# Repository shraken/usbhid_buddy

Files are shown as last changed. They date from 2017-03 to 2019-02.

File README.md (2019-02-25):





# Buddy DAQ

Buddy is a free, open source, and low-cost data acquisition (DAQ) instrument.  It has 8 configurable
IO that can be configured for ADC, DAC, PWM, or counter operation.  The device uses USB HID with a 
custom descriptor for communication with the hidapi library on the host system.  The device can be 
configured as either a host polled or asynchronous update mode for maximum flexibility.  Buddy works
on linux, windows, and macOS systems.  

## Docker

Usage of docker is recommended for building the entire project.  A CMakeList file is provided in the head
directory to build the project and generate all support files (documentation, coverage reports). 

```shell
docker build -t buddy_docker .
docker run -v /path/to/usbhid_buddy:/docker -it buddy_docker /bin/bash
```

this will launch a Docker bash shell and then you build.

```shell
cd /docker
mkdir -p build
cd build
cmake ..
make
```

## Firmware

The firmware is written in C for the Silicon Labs C8051F380/EFM8UB2 chip and is in the `fw` directory.  The
firmware requires a Keil C51 compiler to be used for building.  

The open-source [gboot](https://github.com/shraken/gboot) bootloader written by Gabriele Gorla of gglabs (http://gglabs.us) is used for the buddy device. 

## Hardware

The hardware is developed using the KiCad EDA tool.  The manafacturing, source, and schematic
files are provided in the hw/ directory.

The pin mapping for the standard Bus Pirate 10-pin harness is provided below:

| Color         | Mapping   | Pin #  |
| ------------- |:---------:|:------:|
| Brown         | IN7       |     2  |
| Red           | GND       |     1  |
| Orange        | IN6       |     4  |
| Yellow        | IN5       |     3  |
| Green         | IN0       |     6  |
| Blue          | IN4       |     5  |
| Purple        | IN2       |     8  |
| Grey          | IN1       |     7  |
| White         | 3.3V      |    10  |
| Black         | IN3       |     9  |

## Software

The host software uses the free and open source hidapi library for driverless
operation.  The examples provided build with the hidapi libray itself and
are tested on Linux, Windows, and mac OS systems.

For building the host examples, the hidapi submodule must be cloned with the
following command:

`git submodule update --init`

or when cloning the buddy repo with:

`git clone --recursive https://github.com/shraken/usbhid_buddy.git`

## Tests

The `tests` directory contains the unit tests.  The [Catch2](https://github.com/catchorg/Catch2) test
framework is used for all unit tests.  To manually build and run the unit test, run the following:

```shell
cd tests/
mkdir -p build
cd build
cmake ..
make
./testLibBuddy
```

## Code Coverage

The build server runs gcov/lcov to generate the coverage figure.  You can collect these results manually
by running the following (from the build directory in `tests`):

```shell
lcov -c -d CMakeFiles -out cov.info
genhtml cov.info -o out
open out/index.html
```

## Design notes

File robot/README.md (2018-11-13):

# Buddy Test Platform

This repo contains the manufacturing automated test system for the Buddy USB HID DAQ hardware
device.  

The automated test board mates with a Teensy 3.6 microcontroller for measurement and
stimulus of the "Buddy" DAQ under test.
 - `teensy/` - teensy Arduino firmware for the DUT test software
 - `sw/` - host based robot framework source files to be run by tester
 - `hw/` - PCB schematic, layout, and datasheet files

# Requirements

Install the [ADC](https://github.com/pedvide/ADC) library for the Arduino software.  

# Building

There is no automated build procedure.  

1. Open Arduino IDE 

Modify the `RingBuffer.h` file and set the define `RING_BUFFER_DEFAULT_BUFFER_SIZE` to 4096.  This
requires modification of the `RingBuffer.h` file provided in the `ADC` library installed above.  

# Usage

on Windows

```shell
cd sw/
./run_tests.bat
```

on Linux and Mac OS

```shell
cd sw/
./run_tests.sh
```

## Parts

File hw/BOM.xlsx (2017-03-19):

Id | Designator | Package | Quantity | Designation | Supplier and ref | Cost (quantity 1) | Total Cost | Comments
1 | R5,R2,R8,R9,R3,R14 | R_0603_HandSoldering | 6 | 1k | 667-ERJ-3EKF1001V | 0.15 | 0.9
2 | C1,C3,C6,C7,C10,C11,C12,C13,C16 | C_0603_HandSoldering | 9 | 100nF | 81-GRM39X104K25 | 0.1 | 0.9
3 | C2,C4,C5,C9 | C_0805_HandSoldering | 4 | 1uF | 810-C2012X7R1E105K | 0.14 | 0.56
4 | C8,C14 | C_0603_HandSoldering | 2 | 1uF | 81-GRM188R61E105KA12 | 0.1 | 0.2
5 | C15 | C_0603_HandSoldering | 1 | 10uF | 81-GRM188R60J106KE7D | 0.13 | 0.13
6 | C10 | C_0603_HandSoldering | 1 | 4.7uF | 81-GRM18R60J475KE19D | 0.11 | 0.11
7 | R1 | R_0603_HandSoldering | 1 | 100R | 660-RK73H1JTTD1000F | 0.1 | 0.1
8 | R2,R3,R5,R8,R9,R14 | R_0603_HandSoldering | 6 | 1k | 667-ERJ-3GEYJ102V | 0.1 | 0.6
9 | R6,R7,R10,R15,R16,R17 | R_0603_HandSoldering | 6 | 10k | 667-ERJ-3GEYJ103V | 0.1 | 0.6
10 | R11 | R_0603_HandSoldering | 1 | 0R_NM | 667-ERJ-3GEY0R00V |  | 0 | NM
11 | R4,R12,R13 | R_0603_HandSoldering | 3 | 0R | 667-ERJ-3GEY0R00V | 0.1 | 0.3
12 | D1,D2 | LED_0603 | 2 | LED | 720-LGQ396A3964 | 0.19 | 0.38
13 | D3 | PRTR5V0U2X,215 | 1 | PRTR5V0U2X,215 | 771-PRTR5V0U2X-T/R | 0.52 | 0.52
14 | D4,D5,D6,D7,D8,D9,D10,D11 | SOT-23 | 8 | D_Schottky_x2_Serial_AKC | 512-BAT54S | 0.24 | 1.92
15 | DN1 | LTST-C195KGJRKT | 1 | LTST-C195KGJRKT | 859-LTST-C195KGJRKT | 0.4 | 0.4
16 | F1 | R_1206 | 1 | 1206L050/15YR | 576-1206L075/13.2WR | 0.49 | 0.49
17 | U1 | SOT-23-5 | 1 | MCP1802T-3302I/OT | 579-MCP1802T-3302IOT | 0.58 | 0.58
18 | U2 | LQFP-48_7x7mm_Pitch0.5mm | 1 | C8051F380 | 634-8UB20F64GAQFP48 | 1.9 | 1.9
19 | U3 | TSSOP-20_4.4x6.5mm_Pitch0.65mm | 1 | TLV5630 | 595-TLV5630IPW | 20.12 | 20.12
20 | U4 | VSSOP8-DGK | 1 | TPS60241 | 595-TPS60241DGKR | 1.63 | 1.63
21 | U5 | SOT-23 | 1 | REF3325AIDBZR | 595-REF3325AIDBZR | 1.8 | 1.8
22 | U6 | TSSOP-8_4.4x3mm_Pitch0.65mm | 1 | 23LC1024-I/ST | 579-23LC1024-I/ST | 2.57 | 2.57
23 | U7,U8 | SOT-23-5 | 2 | 74AHC1G125 | 595-SN74AHC1G125DBVR | 0.41 | 0.82
24 | USB1 | microb_usb_top_mount | 1 | MICRO-B_USB | 538-47346-1001 | 0.73 | 0.73
25 | SW1,SW2 | SKRKAEE010 | 2 | SKRKAEE010 | 688-SKRKAE | 0.48 | 0.96
26 | P1 | Socket_Strip_Straight_1x02 | 1 | CONN_01X02 |  |  | 0
27 | P2 | Socket_Strip_Straight_1x03 | 1 | CONN_01X03 |  |  | 0 | NM
28 | P3 | Molex_PicoBlade_53261-0371 | 1 | CONN_01X03 | 538-53261-0371 | 0.9 | 0 | NM
29 | P4 | Socket_Strip_Angled_2x05 | 1 | CONN_02X05 | 571-5103308-1 | 0.74 | 0.74 | NM
 |  |  |  |  |  | parts total | 39.96
 | Manafacturing |  |  |  |  | placements | 68
 | Board Size: |  |  | per |  | unique parts | 29
 | 64x37mm | smartprototyping | $146/100 | 1.46
 |  |  | $1000/1000 | 1
 | Assembly | smallbatchassembly | quantity 100 | 10.74
 |  |  | quantity 1000 | 5.25
 | Others
 |  | Acrylic Case | 110990059 | 3 | https://www.seeedstudio.com/Bus-Pirate-v4-Acrylic-case-kit-v1-p-1417.html
 |  | IDC ribbon cable | CAB-09556 | 4.95 | https://www.sparkfun.com/products/9556
 | total cost | 52.16

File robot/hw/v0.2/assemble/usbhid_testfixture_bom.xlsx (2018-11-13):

Title | usbhid_testfixture |  |  | Digikey
Revision | v0.1
Date | 2017-12-10
Generated | 2017-12-10
Company | Wiggle Labs
Comment 1
Comment 2
Comment 3
Comment 4
Total Parts | 18
Total Unique Parts | 9
Ref | Qty | Value | Footprint
C1 C2 C3 | 3 | 0.1uF | Capacitors_SMD:C_0603_HandSoldering | 399-1096-1-ND
J1 J2 | 2 | Conn_01x14 | Socket_Strips:Socket_Strip_Straight_1x14_Pitch2.54mm | S9195-ND
J3 | 1 | Conn_01x05 | Socket_Strips:Socket_Strip_Straight_1x05_Pitch2.54mm | S6103-ND
J4 | 1 | Conn_02x05_Odd_Even | Socket_Strips:Socket_Strip_Straight_2x05_Pitch2.54mm | A33159-ND
P1 | 1 | BTE-020-01-F-D | samtec:BTE-020-01-F-D-A | SAM10934-ND
R1 R2 R3 R4 R5 | 5 | 10k | Resistors_SMD:R_0603_HandSoldering | 311-10KGRCT-ND
U1 U2 | 2 | MAX335 | Housings_SSOP:TSSOP-24_4.4x7.8mm_Pitch0.65mm | MAX335EUG+-ND
U5 | 1 | MAX4617 | Housings_SSOP:TSSOP-16_4.4x5mm_Pitch0.65mm | MAX4617CUE+CT-ND
U4 U3 | 2 | 74AHC1G125 | TO_SOT_Packages_SMD:SOT-23-5 | 74AHC1G125W5-7DICT-ND
BOM made with KICAD_BOM_WIZARD (https://github.com/HashDefineElectronics/KiCad_BOM_Wizard.git)
Generated 12/10/2017 6:05:52 PM

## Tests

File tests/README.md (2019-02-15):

# Testing

## Unit Tests

We use the Catch-2 test framework to write the unit tests.  The unit tests test the internal logic
and mock out physical hardware access with dummy stubs that we can check were called.  

The units test are written for the following components:
 - codec
 - buddy host library

 Future:
  - firmware
  - python bindings
  - any future language binding

The unit tests are configured to run with the CI and a coverage report is generated and reported on
coveralls hosted site.  Future plan for manual HTML generation are being made.

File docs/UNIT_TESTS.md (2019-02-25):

lib/libbuddy/
 - utility(.h/.c):
  * debug_init
  * debug_write
  * debug_cleanup

 - usbhid_buddy(.h/.c):
  x * reset_codec
  x * encode
  x * decode
  * hidapi_init
  * buddy_write_raw
  * buddy_write_packet
  * buddy_read_packet
  * buddy_send_generic
  * buddy_read_generic
  * buddy_read_generic_noblock
  * buddy_send_pwm
  * buddy_send_dac
  * buddy_read_counter
  * buddy_read_adc
  * buddy_read_adc_noblock
  * buddy_clear
  * buddy_flush
  * buddy_count_channels
  * buddy_configure
  * buddy_get_response
  * buddy_reset_device
  * buddy_get_firmware_info
  * buddy_init
  * buddy_trigger
  * buddy_cleanup

 - support(.h/.c):
  x * swap_uint16
  x * swap_int16
  x * swap_uint32
  x * swap_int32
  x * short_sleep

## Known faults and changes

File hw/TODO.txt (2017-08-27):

v0.5:

 * make micro USB footprint with slotted holes and replace Molex part
 * fix footprint for ESD USB protection diode
 * fix footprint for bicolor red/green LED DN1
 * fix fotprint for TPS 5V converter
 * add fidiucials
 * revert back to SOT23-5 footprint for tristate buffer SN74AHC1G125
 * establish if polyfuse is appropriate given max current of LDO 3.3V reg
 * add testpad for GPIO that can be used for timing
 * consider adding mezzanine on bottom side of board for future
   expander boards

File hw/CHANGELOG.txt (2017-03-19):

v0.1:
* frist!!! release
----

v0.2:
x1. shrink size back down a bit
x2. see if can get away with a 2 layer with GND and +3.3V pour on TOP/BTTM
x3. footprint fixes
   a. 10 pin header needs a silkscreen outline for pins. center and move over.
x4. fix C8051F380 bad pin 12 with 100R to GND when it really should go
   to VBUS.
x5. footprint for the ESD protection diode is bad needs to be fixed
x6. footprint for +5V regulator/reference should be widened for pads
x7. the location of the 10-pin 2 row header is wacky and should be centered
x8. look into mechanical enclosure for entire unit with eye to remove 
  dual row headers.

  alternatively adopt the bus pirate mech footprint standard.

**RESIZED to BUS PIRATE V3.6 FOOTPRINT**

XX9. (potentially use ADG1414BRUZ-REEL7 as an octal SPST switch to isolate DAC
       and ADC so they can coexist on same pins) or MAX335 or MAX395.

** ATTEMPT IN SOFTWARE TO VERIFY IF DAC CAN BE POWERED OFF AND SAME ATTACHED
  CHANNEL USED AS ADC WITH EXTERNAL VOLTAGE STIMULUS **

not required, will not be implemented in v0.2

x10. USB VBUS power LED indicator
x11. change the micro USB connector out for the EOL Hirose to a a standard SMD
   mount with a non-reversed connector

Amphenol-FCI 10118192-0001LF
609-4613-1-ND
http://www.digikey.com/product-detail/en/10118192-0001LF/609-4613-1-ND/2785378?WT.z_cid=ref_octopart_dkc_buynow&site=us

https://github.com/open-project/kicadlibrary
----

v0.3:
1. rearrange buttons and LEDs to fit the existing enclosure footprint
x2. move 10 pin header back 1.1 mm to fit into enclosure.  size check
x3. fix the USBDP and USBDN routing issue
x4. make footprint for TPS 5V reference larger
-?5. make footprint for dual color LED slightly larger
x6. rounded edge corners
x7. make corner holes larger, 2.7mm -> 3.2mm+ **(made to 3.2mm PAD)
x8. make red/green bicolor LED active low
x9. move ADC0_IN and ADC1_IN to P0.6 and P0.7 for interrupt capability
x10. look into benefit of additional crystal oscillator for timing tolerance improvement
 (added a 32.768 kHz watch crystal for millis timer and ADC sampling trigger clock)
----

v0.4:
x1. add SPI SRAM buffer
?2. fix bad GND pour DRC issued with pin 6 on chip U2.
-3. make USB1 connector to use slotted holes for mechanical robustness (not this revision)
x4. add protection diodes to ADC and DAC channels
x5. add picoblade programming header on bottom of board to mate to C2 adapter board
x6. switch ADC0_IN and ADC1_IN from P0.6 and P0.7 as they can't be allocated for ADC
x7. add a USB polyfuse
x8. add SPI testpads on backside of board
x9. add health indicator LED for 1 second interval flashing
-10. add testpoint for spare GPIO
NO 11. switch red and green bicolor LED back to active high cfg
x12. remove watch crystal
x13. make VREF (P1.5) connected to a 2.5V reference
x14. add MISO connection to read out TLV563x parameters
x15. add tristate buffer to MISO/SOMI lines for TLV563x and 23LC1024 module 
x16. fix incorrect naming scheme, DAC_OUTA = ADC0_IN
NO 17. consider backside mezzanine connector to mate for mating to a breakout DB
	or bulk screw-terminal board.
x18. add 10 uF and 100 pF decoupling cap on PIN16 of TLV563X for internal voltage ref
  as recommended by the datasheet. 
x19. add 4.8 uF and 0.1 uF bypass capacitor on P1.5 reference pin on C8051F380 chip
----

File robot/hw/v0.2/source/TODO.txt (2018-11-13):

v0.2:
 x * resisitive divider from FIO pins on the ADC.  Place the divider network
   on the ADC pin side of the multiplexor.  The divider should bring 5V max
   to 3.3V.
 x * LED indicators on board driven by Teensy to indicate when test is ongoing
 and maybe a visual indicator for pass/fail.
 x * replace teensy 3.2 with teensy 3.6 for the the additional RAM and CPU.
 (NO) consider usage of secondary ADC and DAC as a means to perhaps scan for
  crosstalk measurements.
 x * use +5V logic almost everywhere.  Replace 3.3V with 5.0V on MAX335 and
 MAX4617..
 (THERE) consider SD card access to save logs on teensy?
* test points or some secondary header to expose FIO_0 - FIO_7 for
saleae analyzer.

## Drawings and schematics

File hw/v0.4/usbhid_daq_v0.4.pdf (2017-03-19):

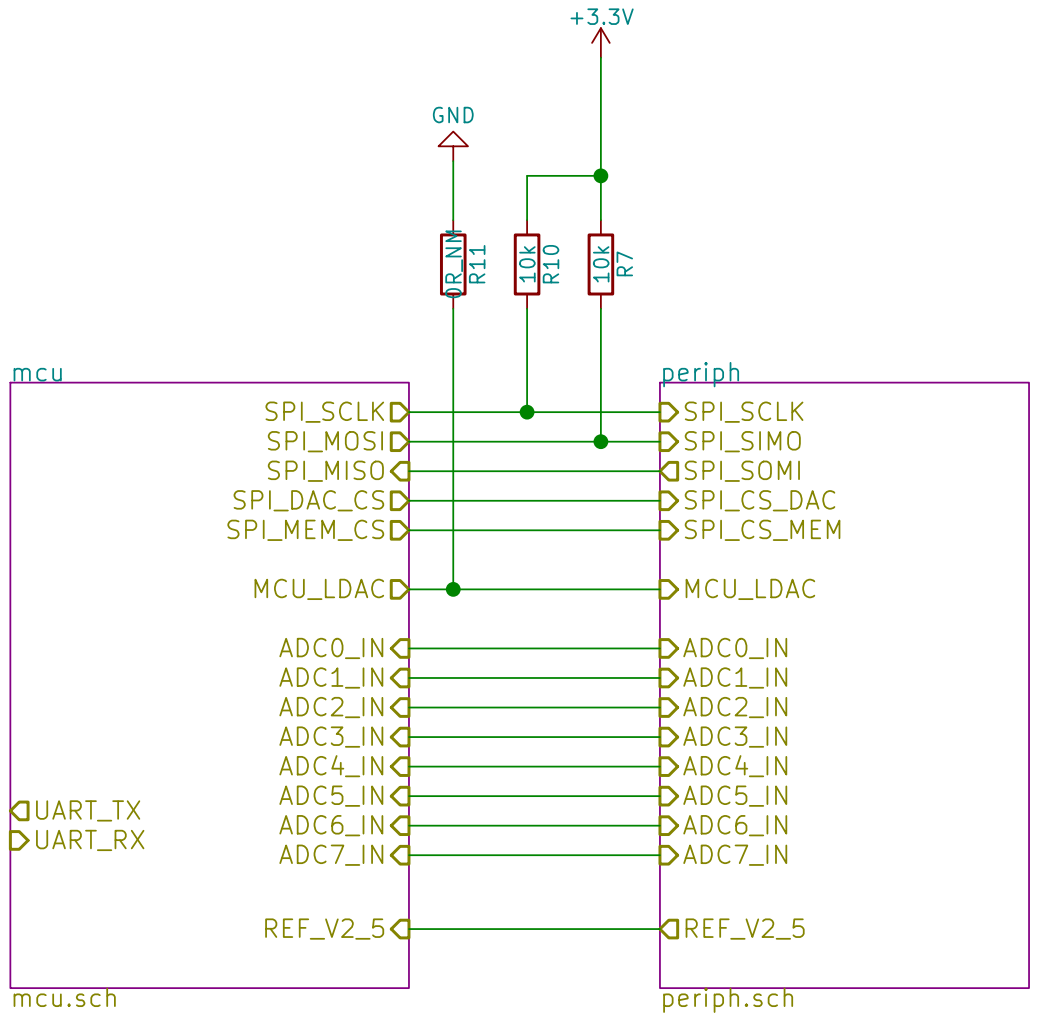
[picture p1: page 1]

File: usbhid_daq.sch Sheet: / Wiggle Labs

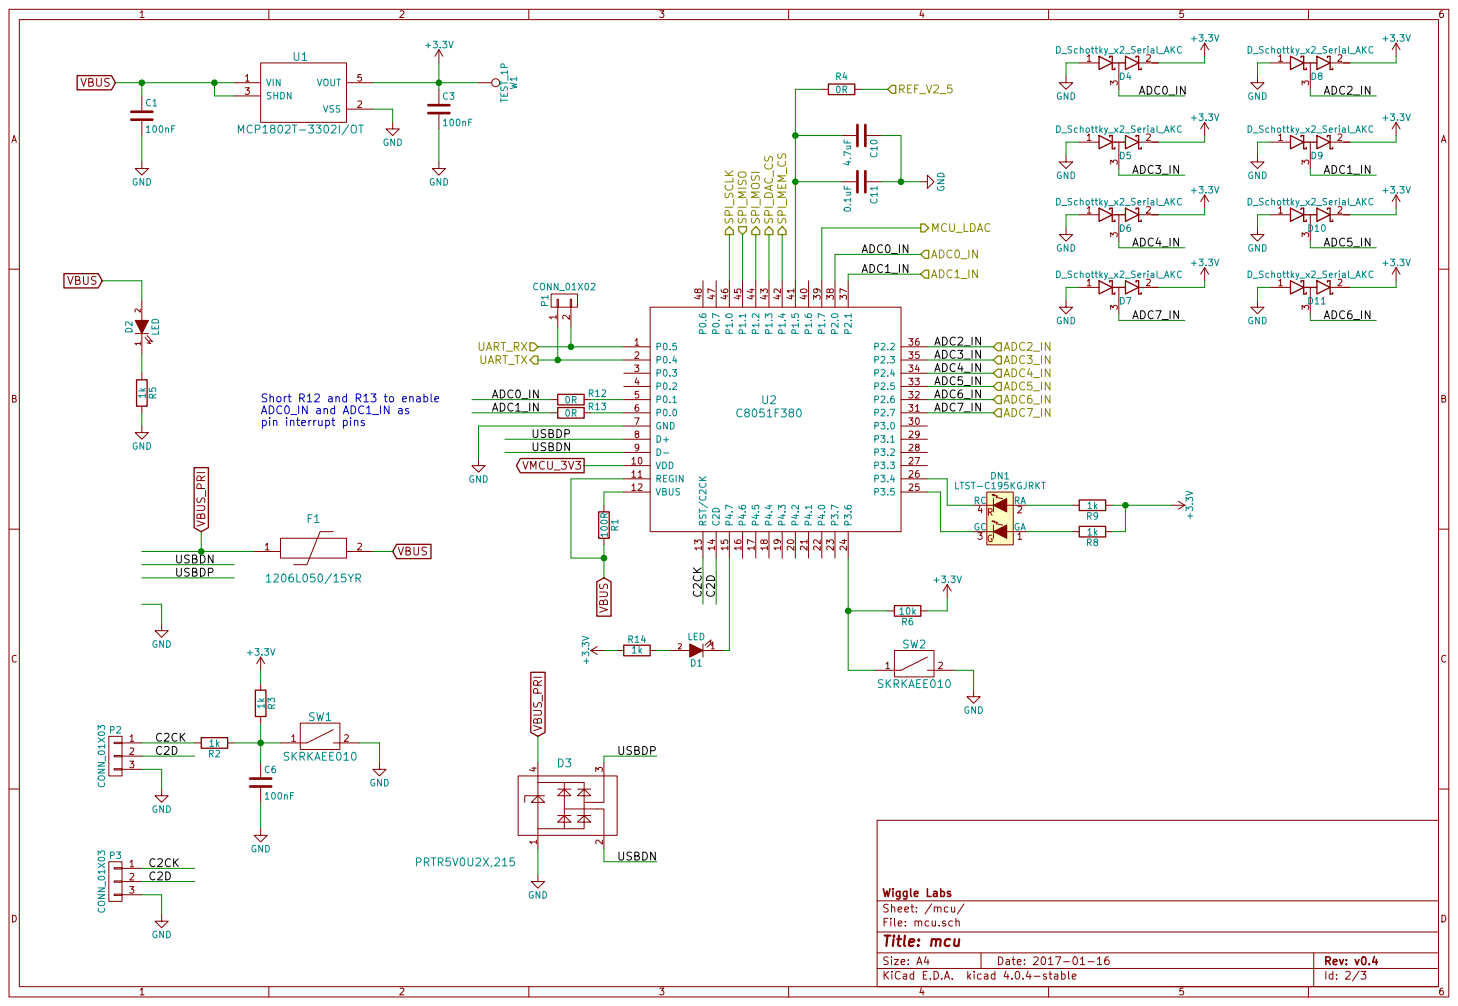
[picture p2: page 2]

1 2 D2 LED 1kR5 GND VBUS VBUS

Short R12 and R13 to enable
ADC0_IN and ADC1_IN as

File: mcu.sch Sheet: /mcu/ Wiggle Labs

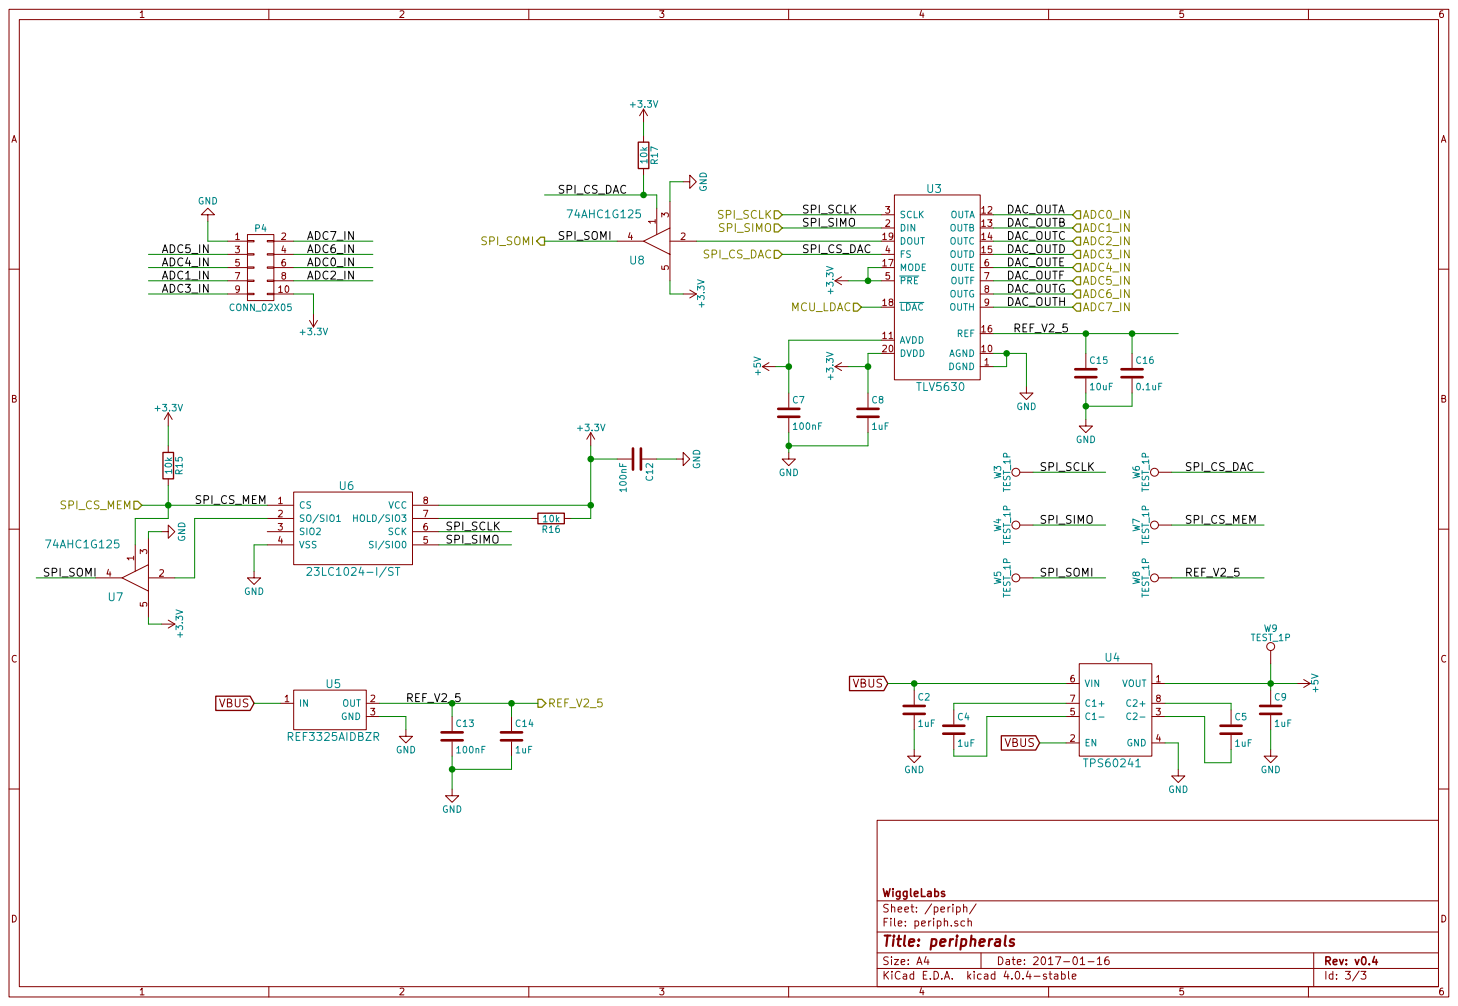
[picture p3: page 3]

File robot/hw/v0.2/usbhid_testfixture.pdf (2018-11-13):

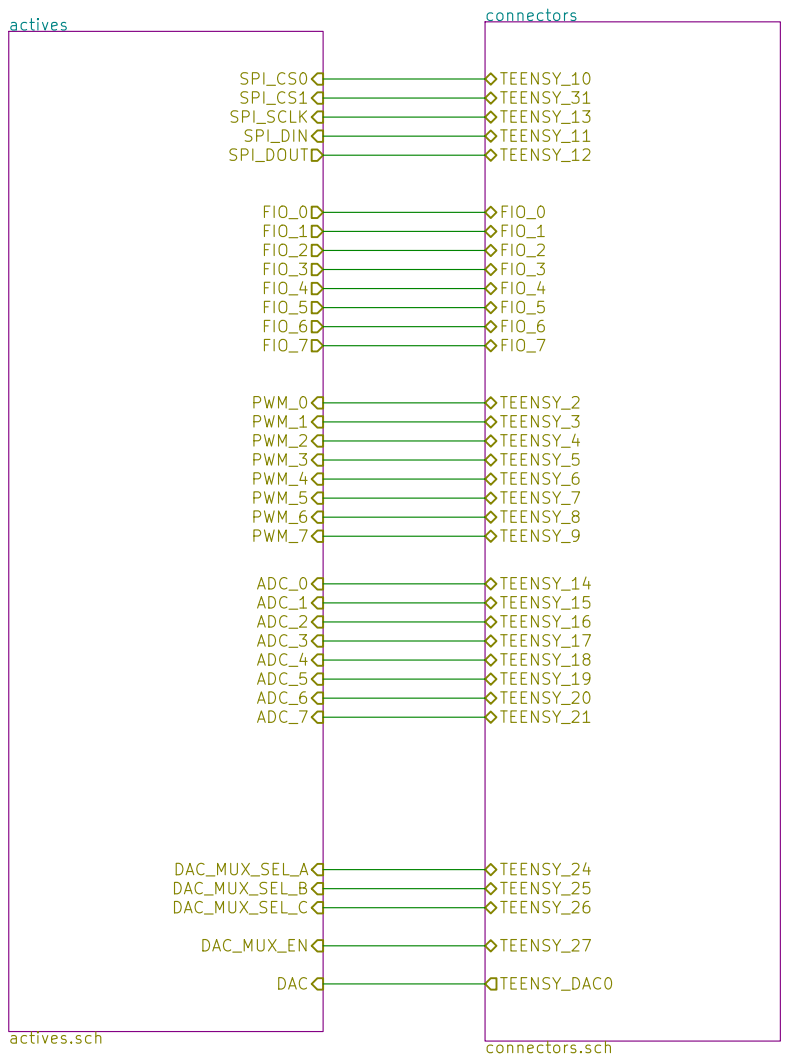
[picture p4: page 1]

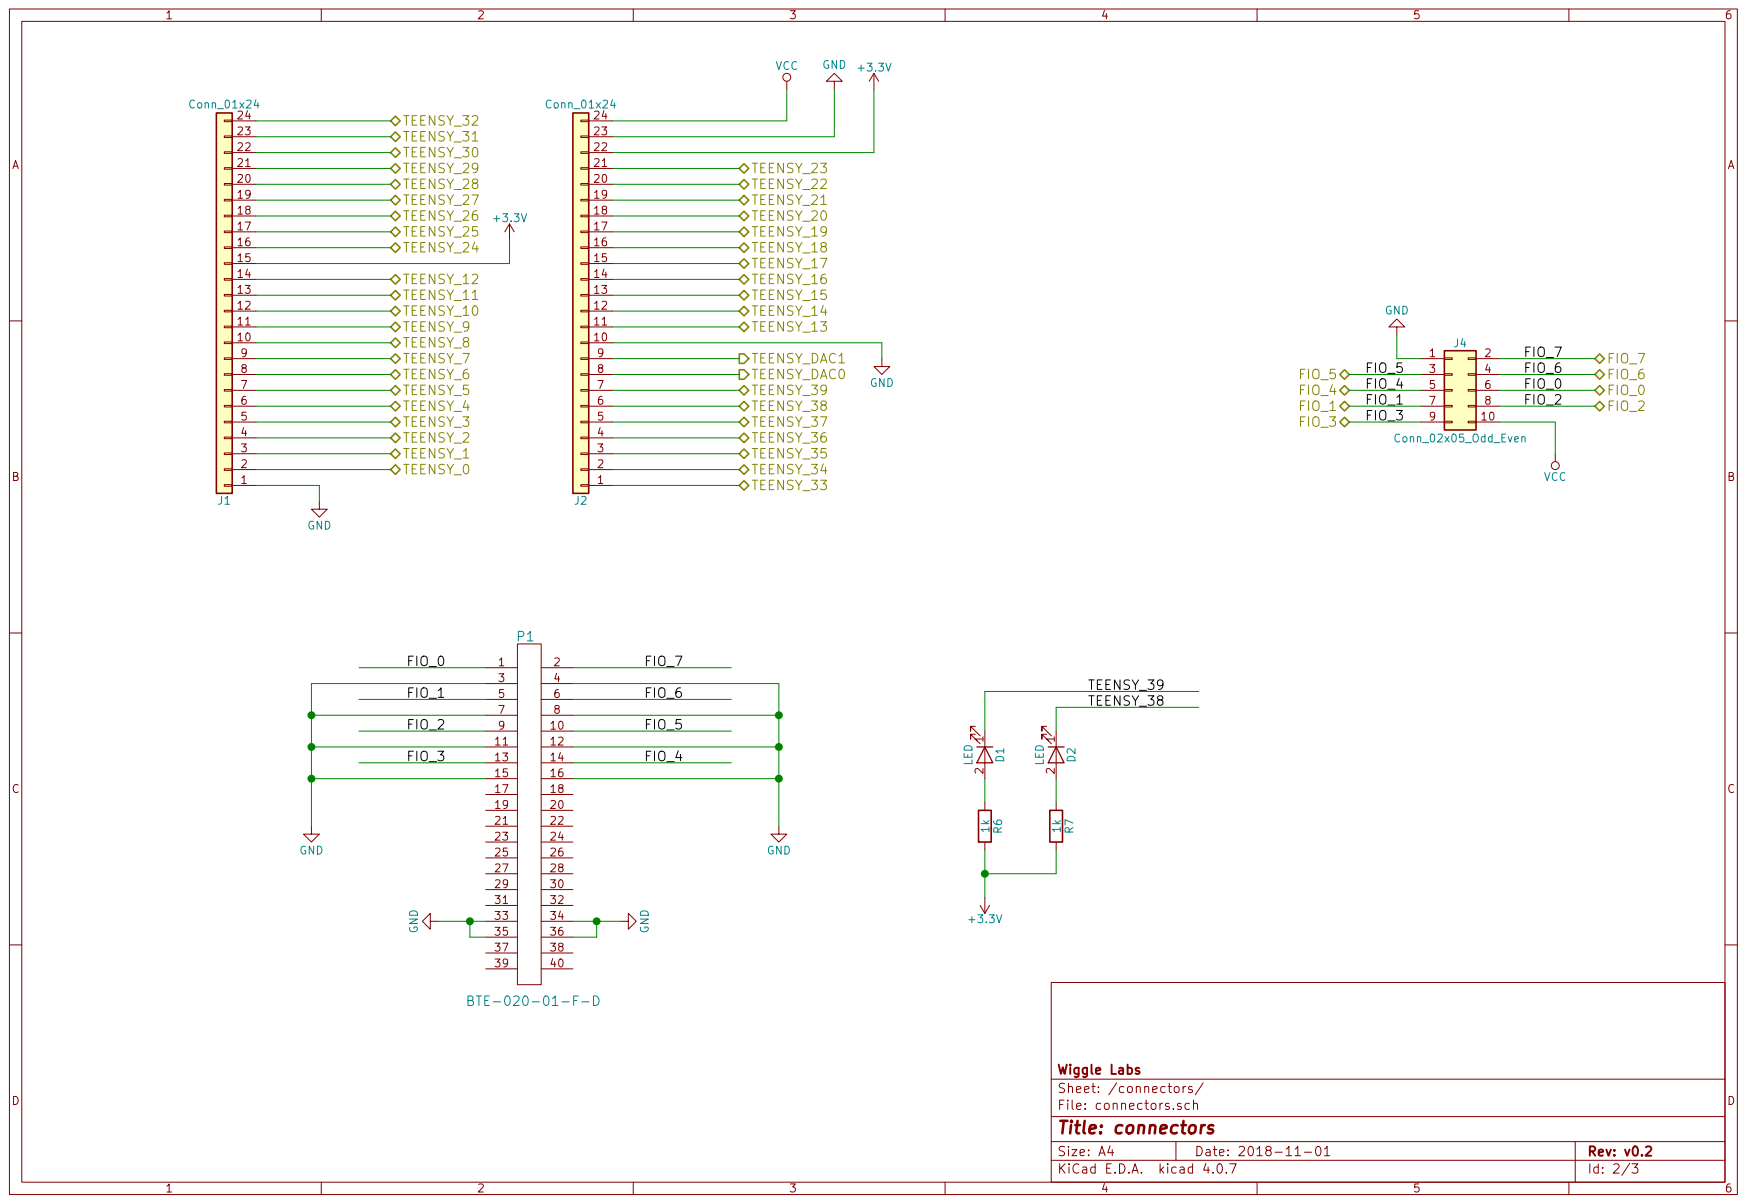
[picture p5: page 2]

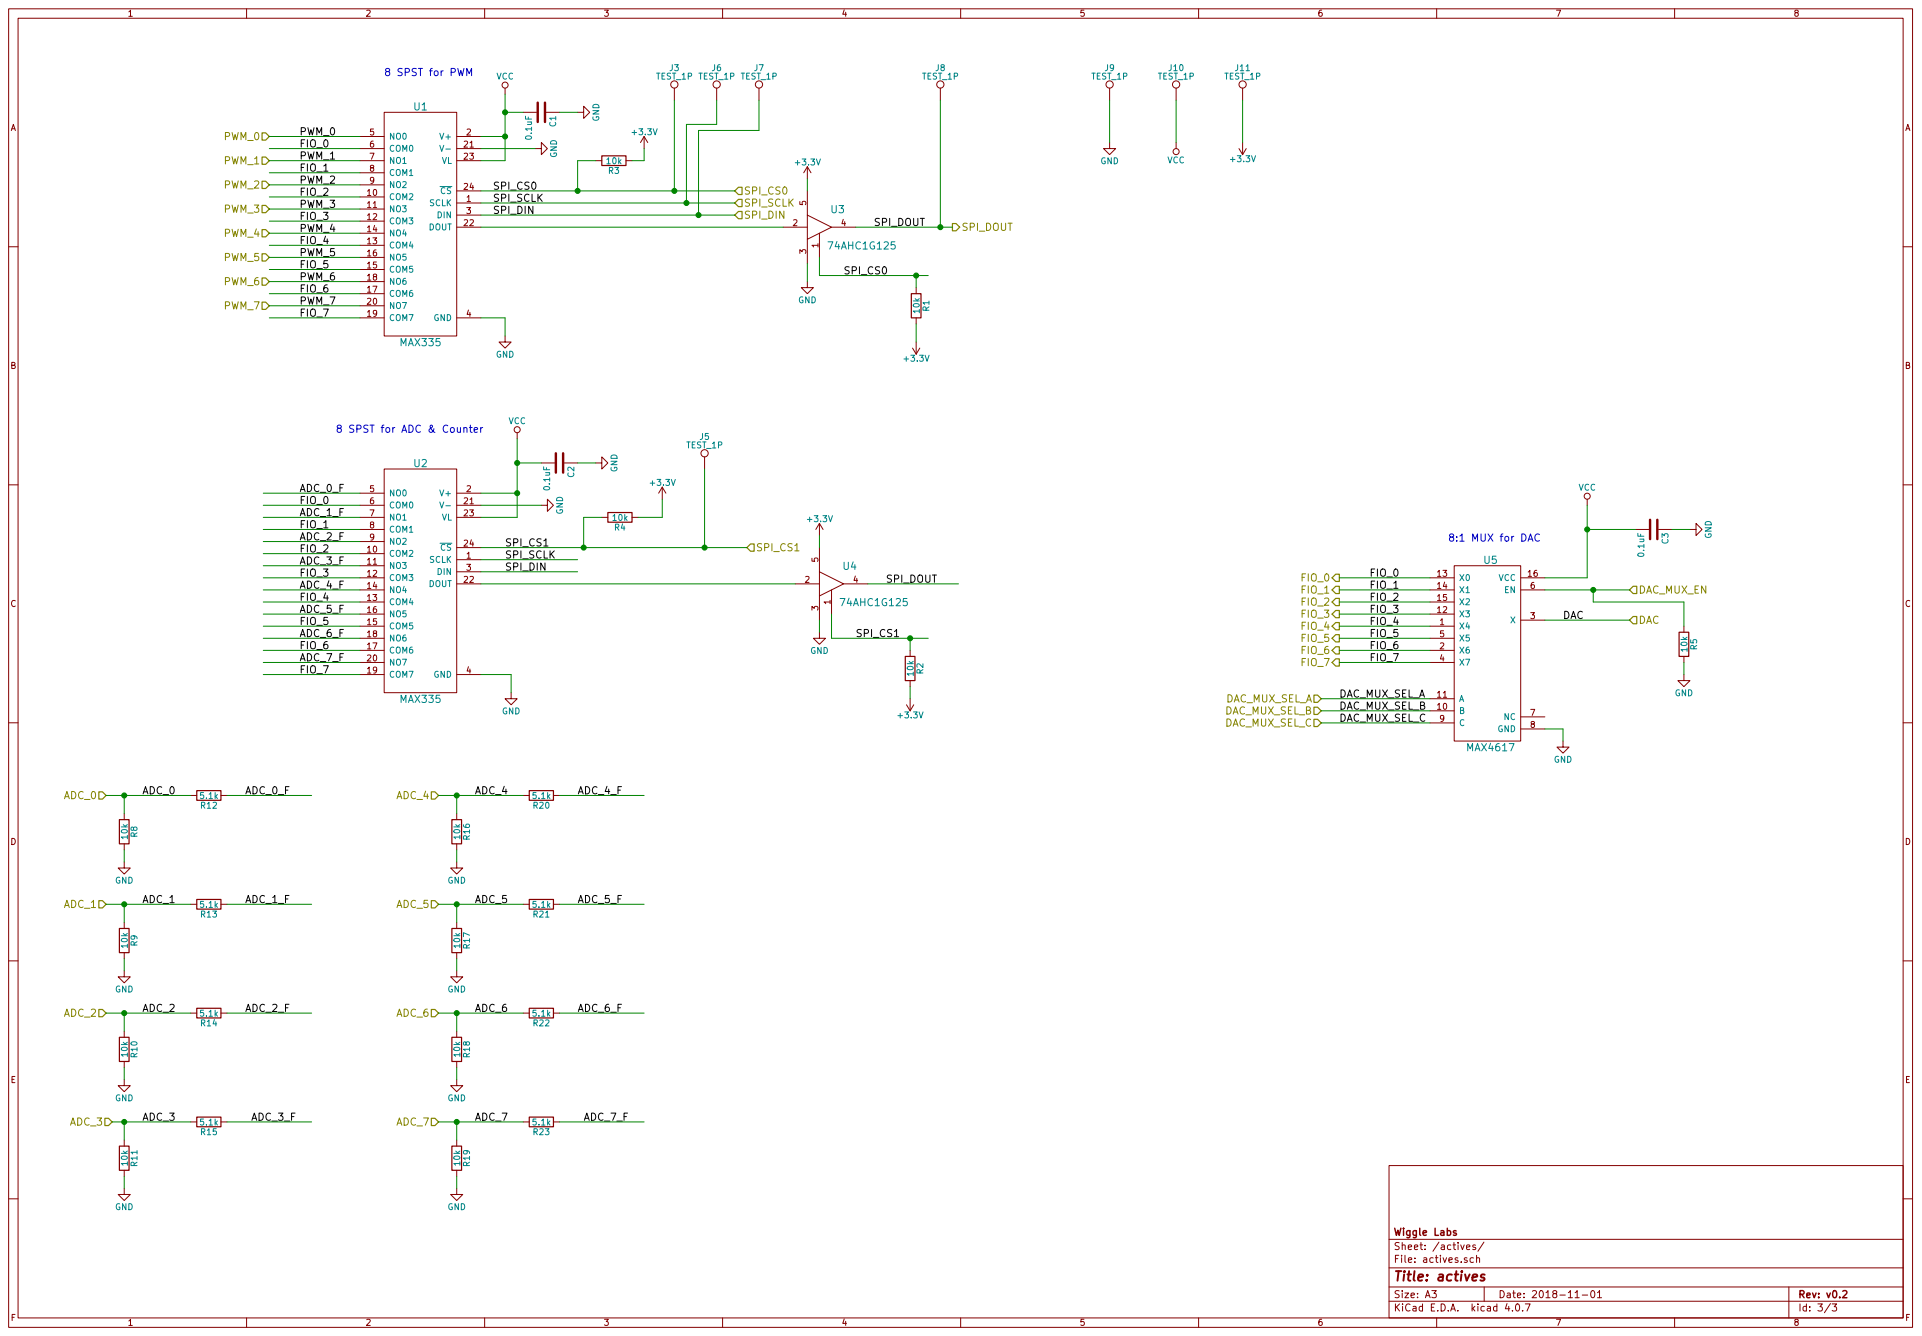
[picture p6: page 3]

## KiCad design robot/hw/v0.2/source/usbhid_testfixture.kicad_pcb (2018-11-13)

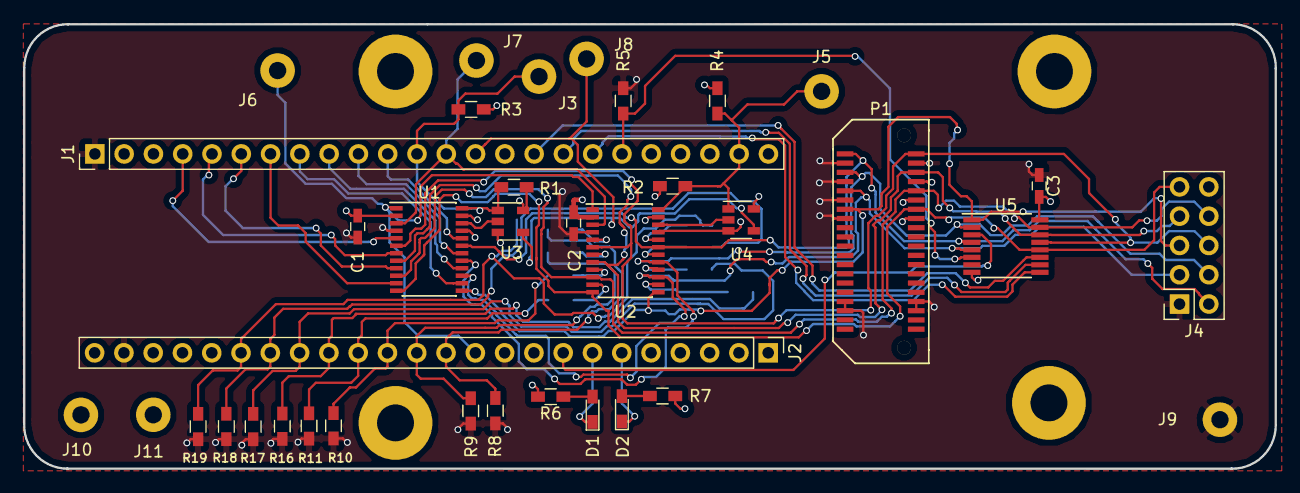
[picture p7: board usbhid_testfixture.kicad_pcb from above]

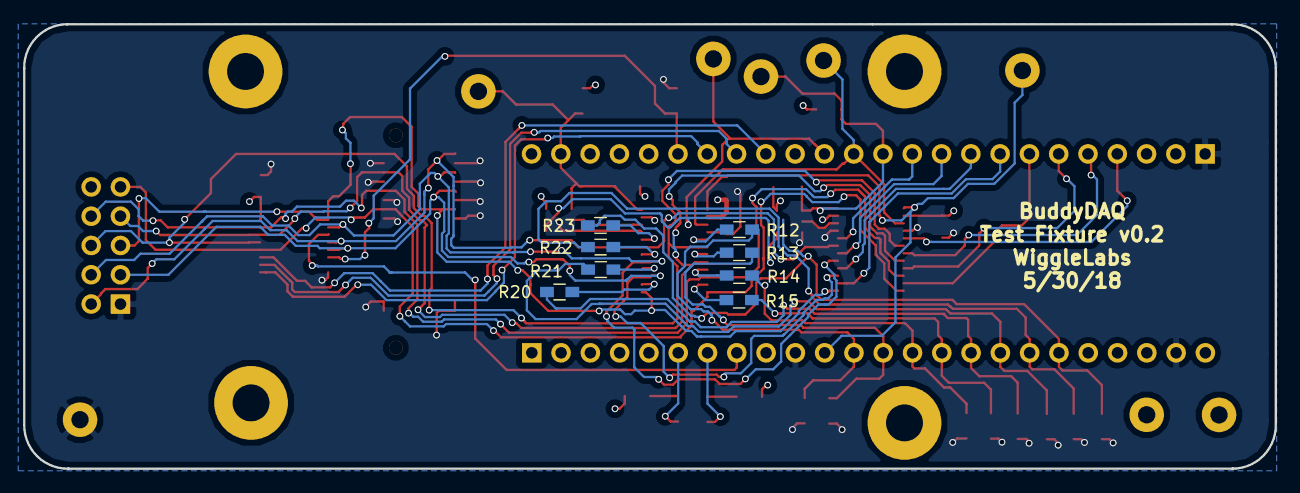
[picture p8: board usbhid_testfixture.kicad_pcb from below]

Board: 4 copper layers, 108.5 x 38.5 mm, 45 parts (8 on the bottom side), 51 nets.

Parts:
C1, C2, C3: 0.1uF; C_0603_HandSoldering
D1, D2: LED; LED_0603_HandSoldering
J1, J2: Conn_01x24; Pin_Header_Straight_1x24_Pitch2.54mm
J3, J5, J6, J7, J8, J9, J10, J11: TEST_1P; Measurement_Point_Round-TH_Big
J4: Conn_02x05_Odd_Even; Socket_Strip_Straight_2x05_Pitch2.54mm
P1: BTE-020-01-F-D; BTE-020-01-F-D-A
R1, R2, R3, R4, R5, R8, R9, R10, R11, R16, R17, R18, R19: 10k; R_0603_HandSoldering
R6, R7: 1k; R_0603_HandSoldering
R12, R13, R14, R15, R20, R21, R22, R23: 5.1k; R_0603_HandSoldering
U1, U2: MAX335; TSSOP-24_4.4x7.8mm_Pitch0.65mm
U3, U4: 74AHC1G125; SOT-23-5
U5: MAX4617; TSSOP-16_4.4x5mm_Pitch0.65mm

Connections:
+3V3: J1.15, J2.22, J11.1, R1.2, R2.2, R3.1, R4.1, R6.2, R7.2, U3.5, U4.5
/actives/ADC_0: J2.12, R8.1, R12.2
/actives/ADC_0_F: R12.1, U2.5
/actives/ADC_1: J2.13, R9.1, R13.2
/actives/ADC_1_F: R13.1, U2.7
/actives/ADC_2: J2.14, R10.1, R14.2
/actives/ADC_2_F: R14.1, U2.9
/actives/ADC_3: J2.15, R11.1, R15.2
/actives/ADC_3_F: R15.1, U2.11
/actives/ADC_4: J2.16, R16.1, R20.2
/actives/ADC_4_F: R20.1, U2.14
/actives/ADC_5: J2.17, R17.1, R21.2
/actives/ADC_5_F: R21.1, U2.16
/actives/ADC_6: J2.18, R18.1, R22.2
/actives/ADC_6_F: R22.1, U2.18
/actives/ADC_7: J2.19, R19.1, R23.2
/actives/ADC_7_F: R23.1, U2.20
/actives/DAC: J2.8, U5.3
/actives/DAC_MUX_EN: J1.19, R5.1, U5.6
/actives/DAC_MUX_SEL_A: J1.16, U5.11
/actives/DAC_MUX_SEL_B: J1.17, U5.10
/actives/DAC_MUX_SEL_C: J1.18, U5.9
/actives/FIO_0: J4.6, P1.1, U1.6, U2.6, U5.13
/actives/FIO_1: J4.7, P1.5, U1.8, U2.8, U5.14
/actives/FIO_2: J4.8, P1.9, U1.10, U2.10, U5.15
/actives/FIO_3: J4.9, P1.13, U1.12, U2.12, U5.12
/actives/FIO_4: J4.5, P1.14, U1.13, U2.13, U5.1
/actives/FIO_5: J4.3, P1.10, U1.15, U2.15, U5.5
/actives/FIO_6: J4.4, P1.6, U1.17, U2.17, U5.2
/actives/FIO_7: J4.2, P1.2, U1.19, U2.19, U5.4
/actives/PWM_0: J1.4, U1.5
/actives/PWM_1: J1.5, U1.7
/actives/PWM_2: J1.6, U1.9
/actives/PWM_3: J1.7, U1.11
/actives/PWM_4: J1.8, U1.14
/actives/PWM_5: J1.9, U1.16
/actives/PWM_6: J1.10, U1.18
/actives/PWM_7: J1.11, U1.20
/actives/SPI_CS0: J1.12, J3.1, R1.1, R3.2, U1.24, U3.1
/actives/SPI_CS1: J1.23, J5.1, R2.1, R4.2, U2.24, U4.1
/actives/SPI_DIN: J1.13, J7.1, U1.3, U2.3
/actives/SPI_DOUT: J1.14, J8.1, U3.4, U4.4
/actives/SPI_SCLK: J2.11, J6.1, U1.1, U2.1
/connectors/TEENSY_38: D2.1, J2.6
/connectors/TEENSY_39: D1.1, J2.7
GND: C1.1, C2.1, C3.1, J1.1, J2.10, J2.23, J4.1, J9.1, P1.3, P1.4, P1.7, P1.8, P1.11, P1.12, P1.15, P1.16, P1.33, P1.34, P1.35, P1.36, R5.2, R8.2, R9.2, R10.2, R11.2, R16.2, R17.2, R18.2, R19.2, U1.4, U1.21, U2.4, U2.21, U3.3, U4.3, U5.8
unnamed: D1.2, R6.1
unnamed: D2.2, R7.1
unnamed: U1.22, U3.2
unnamed: U2.22, U4.2
VCC: C1.2, C2.2, C3.2, J2.24, J4.10, J10.1, U1.2, U1.23, U2.2, U2.23, U5.16

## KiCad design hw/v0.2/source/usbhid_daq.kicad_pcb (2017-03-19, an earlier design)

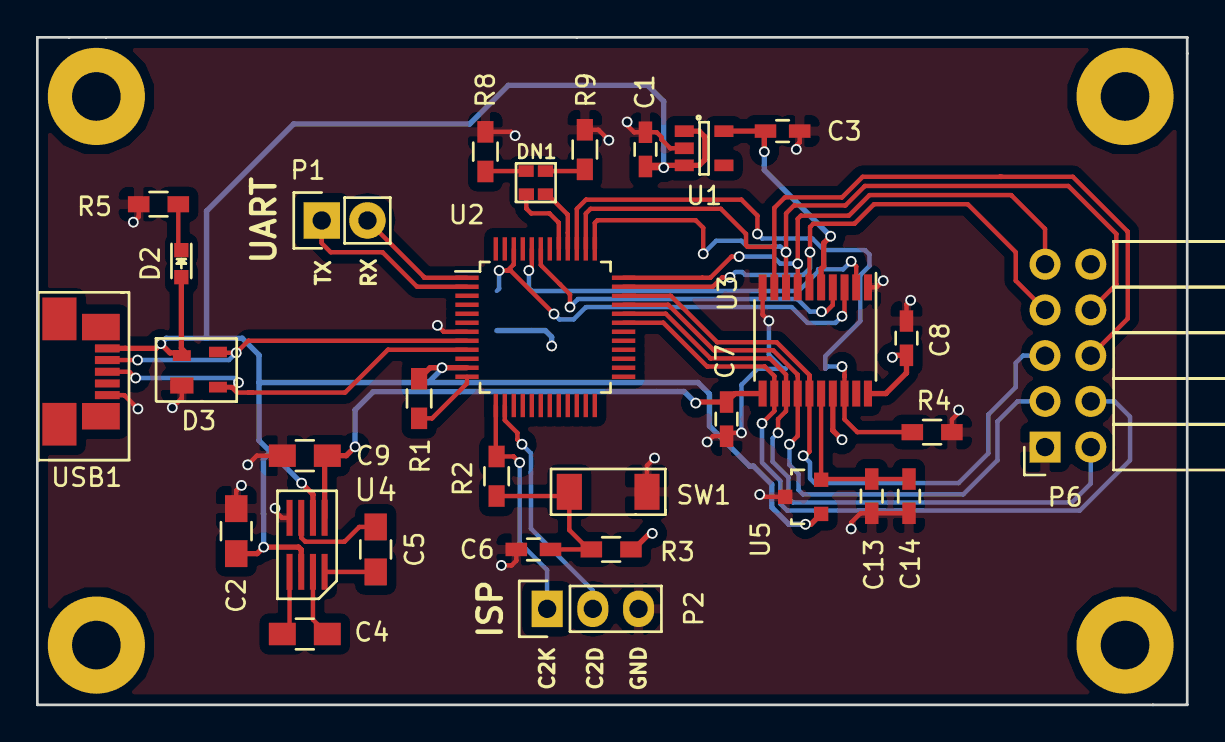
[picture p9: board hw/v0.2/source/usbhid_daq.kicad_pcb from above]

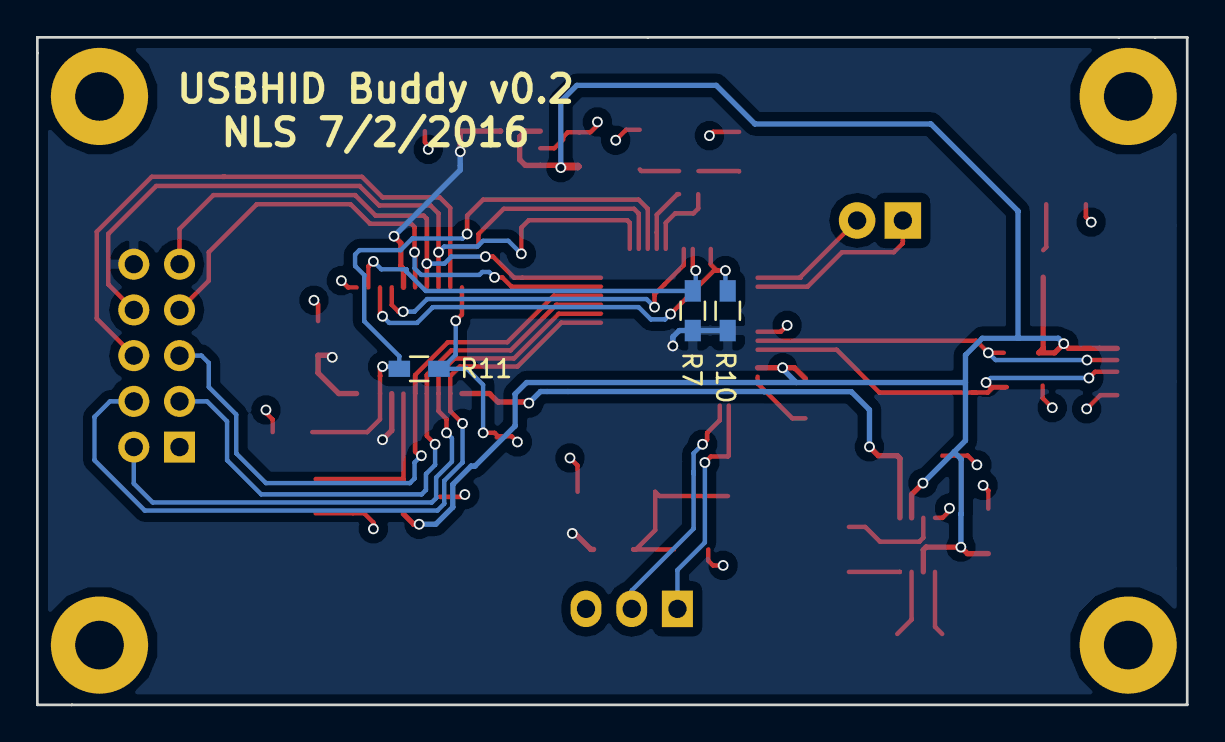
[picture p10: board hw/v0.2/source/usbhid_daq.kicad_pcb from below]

Board: 2 copper layers, 63.9 x 37.1 mm, 34 parts (3 on the bottom side), 34 nets.

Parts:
C1, C6, C7, C13: 100nF; C_0603_HandSoldering
C2, C4, C5, C9: 1uF; C_0805_HandSoldering
C3: C3; C_0603_HandSoldering
C8, C14: 1uF; C_0603_HandSoldering
D2: LED; LED_0603
D3: PRTR5V0U2X,215
DN1: LTST-C195KGJRKT
P1: CONN_01X02; Socket_Strip_Straight_1x02
P2: CONN_01X03; Socket_Strip_Straight_1x03
P6: CONN_02X05; Socket_Strip_Angled_2x05
R1: 100R; R_0603_HandSoldering
R2, R3, R5, R8, R9: 1k; R_0603_HandSoldering
R4: 0R; R_0603_HandSoldering
R7, R10: 10k; R_0603_HandSoldering
R11: 0R_NM; R_0603_HandSoldering
SW1: SKRKAEE010
U1: MCP1802T-3302I/OT; SOT-23-5
U2: C8051F380; LQFP-48_7x7mm_Pitch0.5mm
U3: TLV5630; TSSOP-20_4.4x6.5mm_Pitch0.65mm
U4: TPS60241; VSSOP8-DGK
U5: REF3325AIDBZR; SOT-23
USB1: MICRO-B_USB; microb_usb_top_mount

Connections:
+3V3: C3.1, C8.1, P6.10, R3.1, R7.1, R10.1, U1.5, U3.5, U3.17, U3.20
+5V: C7.1, C9.1, U3.11, U4.1
/mcu/ADC0_IN: P6.6, U2.38, U3.9
/mcu/ADC1_IN: P6.8, U2.37, U3.8
/mcu/ADC2_IN: P6.9, U2.36, U3.7
/mcu/ADC3_IN: P6.7, U2.35, U3.6
/mcu/ADC4_IN: P6.5, U2.34, U3.15
/mcu/ADC5_IN: P6.3, U2.33, U3.14
/mcu/ADC6_IN: P6.2, U2.32, U3.13
/mcu/ADC7_IN: P6.4, U2.31, U3.12
/mcu/C2CK: P2.1, R2.2, U2.13
/mcu/C2D: P2.2, U2.14
/mcu/MCU_LDAC: R4.1, R11.2, U2.39, U3.18
/mcu/SPI_CS: U2.43, U3.4
/mcu/SPI_MOSI: R7.2, U2.44, U3.2
/mcu/SPI_SCLK: R10.2, U2.46, U3.3
/mcu/UART_RX: P1.2, U2.1
/mcu/UART_TX: P1.1, U2.2
/mcu/USBDN: D3.3, U2.8, USB1.2
/mcu/USBDP: D3.2, U2.9, USB1.3
/periph/DAC_REF_V2_5: C13.1, C14.1, U3.16, U5.2
GND: C1.2, C2.2, C3.2, C6.2, C7.2, C8.2, C9.2, C13.2, C14.2, D3.1, P2.3, P6.1, R4.2, R5.2, R8.1, R9.1, R11.1, SW1.2, U1.2, U2.7, U3.1, U3.10, U4.4, U5.3, USB1.5
unnamed: C4.1, U4.7
unnamed: C4.2, U4.5
unnamed: C5.1, U4.8
unnamed: C5.2, U4.3
unnamed: C6.1, R2.1, R3.2, SW1.1
unnamed: D2.1, R5.1
unnamed: DN1.1, U2.40
unnamed: DN1.2, U2.41
unnamed: DN1.3, R9.2
unnamed: DN1.4, R8.2
unnamed: R1.1, U2.12
VBUS: C1.1, C2.1, D2.2, D3.4, R1.2, U1.1, U1.3, U2.11, U4.2, U4.6, U5.1, USB1.1

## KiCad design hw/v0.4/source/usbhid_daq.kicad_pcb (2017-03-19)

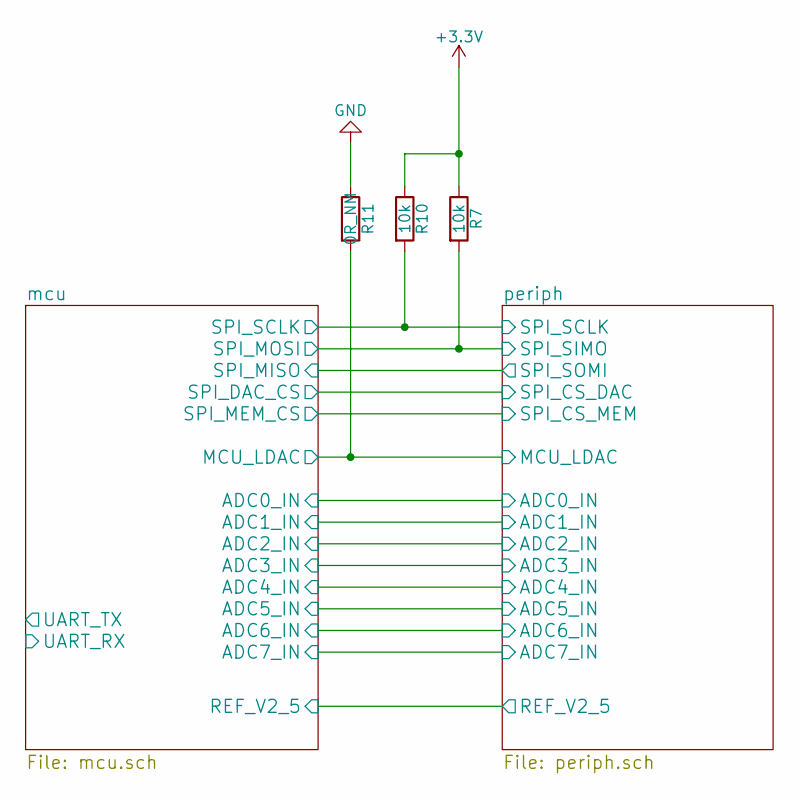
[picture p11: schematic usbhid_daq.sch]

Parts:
R7, R10: 10k; R_0603_HandSoldering
R11: 0R_NM; R_0603_HandSoldering

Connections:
+3V3: R7.1, R10.1; also elsewhere on the board
/mcu/MCU_LDAC: R11.2; also elsewhere on the board
/mcu/SPI_MOSI: R7.2; also elsewhere on the board
/mcu/SPI_SCLK: R10.2; also elsewhere on the board
GND: R11.1; also elsewhere on the board

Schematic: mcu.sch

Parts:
C1, C3, C6: 100nF; C_0603_HandSoldering
C10: 4.7uF; C_0603_HandSoldering
C11: 0.1uF; C_0603_HandSoldering
D1, D2: LED; LED_0603
D3: PRTR5V0U2X,215
D4, D5, D6, D7, D8, D9, D10, D11: D_Schottky_x2_Serial_AKC; SOT-23
DN1: LTST-C195KGJRKT
F1: 1206L050/15YR; R_1206
P1: CONN_01X02; Socket_Strip_Straight_1x02
P2: CONN_01X03; Socket_Strip_Straight_1x03
P3: CONN_01X03; Molex_PicoBlade_53261-0371
R1: 100R; R_0603_HandSoldering
R2, R3, R5, R8, R9, R14: 1k; R_0603_HandSoldering
R4, R12, R13: 0R; R_0603_HandSoldering
R6: 10k; R_0603_HandSoldering
SW1, SW2: SKRKAEE010
U1: MCP1802T-3302I/OT; SOT-23-5
U2: C8051F380; LQFP-48_7x7mm_Pitch0.5mm
USB1: MICRO-B_USB; microb_usb_top_mount
W1: TEST_1P; TESTPAD_SMALL

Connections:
+3V3: C3.1, D4.2 (K), D5.2 (K), D6.2 (K), D7.2 (K), D8.2 (K), D9.2 (K), D10.2 (K), D11.2 (K), R3.1, R6.1, R8.1, R9.1, R14.1, U1.5 (VOUT), W1.1; also elsewhere on the board
/mcu/ADC0_IN: D4.3 (common), R12.2, U2.38 (P2.0); also elsewhere on the board
/mcu/ADC1_IN: D9.3 (common), R13.2, U2.37 (P2.1); also elsewhere on the board
/mcu/ADC2_IN: D8.3 (common), U2.36 (P2.2); also elsewhere on the board
/mcu/ADC3_IN: D5.3 (common), U2.35 (P2.3); also elsewhere on the board
/mcu/ADC4_IN: D6.3 (common), U2.34 (P2.4); also elsewhere on the board
/mcu/ADC5_IN: D10.3 (common), U2.33 (P2.5); also elsewhere on the board
/mcu/ADC6_IN: D11.3 (common), U2.32 (P2.6); also elsewhere on the board
/mcu/ADC7_IN: D7.3 (common), U2.31 (P2.7); also elsewhere on the board
/mcu/C2CK: P2.1, P3.1, R2.2, U2.13 (RST/C2CK)
/mcu/C2D: P2.2, P3.2, U2.14 (C2D)
/mcu/MCU_LDAC: U2.39 (P1.7); also elsewhere on the board
/mcu/REF_V2_5: R4.1; also elsewhere on the board
/mcu/SPI_MISO: U2.45 (P1.1); also elsewhere on the board
/mcu/SPI_MOSI: U2.44 (P1.2); also elsewhere on the board
/mcu/SPI_SCLK: U2.46 (P1.0); also elsewhere on the board
/mcu/UART_RX: P1.2, U2.1 (P0.5)
/mcu/UART_TX: P1.1, U2.2 (P0.4)
/mcu/USBDN: D3.2, U2.9 (D-), USB1.2
/mcu/USBDP: D3.3, U2.8 (D+), USB1.3
/periph/SPI_CS_DAC: U2.43 (P1.3); also elsewhere on the board
/periph/SPI_CS_MEM: U2.42 (P1.4); also elsewhere on the board
GND: C1.2, C3.2, C6.2, C10.1, C11.1, D3.1, D4.1 (A), D5.1 (A), D6.1 (A), D7.1 (A), D8.1 (A), D9.1 (A), D10.1 (A), D11.1 (A), P2.3, P3.3, R5.2, SW1.2, SW2.2, U1.2 (VSS), U2.7 (GND), USB1.5; also elsewhere on the board
unnamed: C6.1, R2.1, R3.2, SW1.1
unnamed: C10.2, C11.2, R4.2, U2.41 (P1.5)
unnamed: D1.1 (K), U2.15 (P4.7)
unnamed: D1.2 (A), R14.2
unnamed: D2.1 (K), R5.1
unnamed: DN1.1 (GA), R8.2
unnamed: DN1.2 (RA), R9.2
unnamed: DN1.3 (GC), U2.25 (P3.5)
unnamed: DN1.4 (RC), U2.26 (P3.4)
unnamed: R1.1, U2.12 (VBUS)
unnamed: R6.2, SW2.1, U2.24 (P3.6)
unnamed: R12.1, U2.5 (P0.1)
unnamed: R13.1, U2.6 (P0.0)
VBUS: C1.1, D2.2 (A), F1.2, R1.2, U1.1 (VIN), U1.3 (SHDN), U2.11 (REGIN); also elsewhere on the board
VBUS_PRI: D3.4, F1.1, USB1.1
VMCU_3V3: U2.10 (VDD)

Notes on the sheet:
Short R12 and R13 to enable ADC0_IN and ADC1_IN as pin interrupt pins

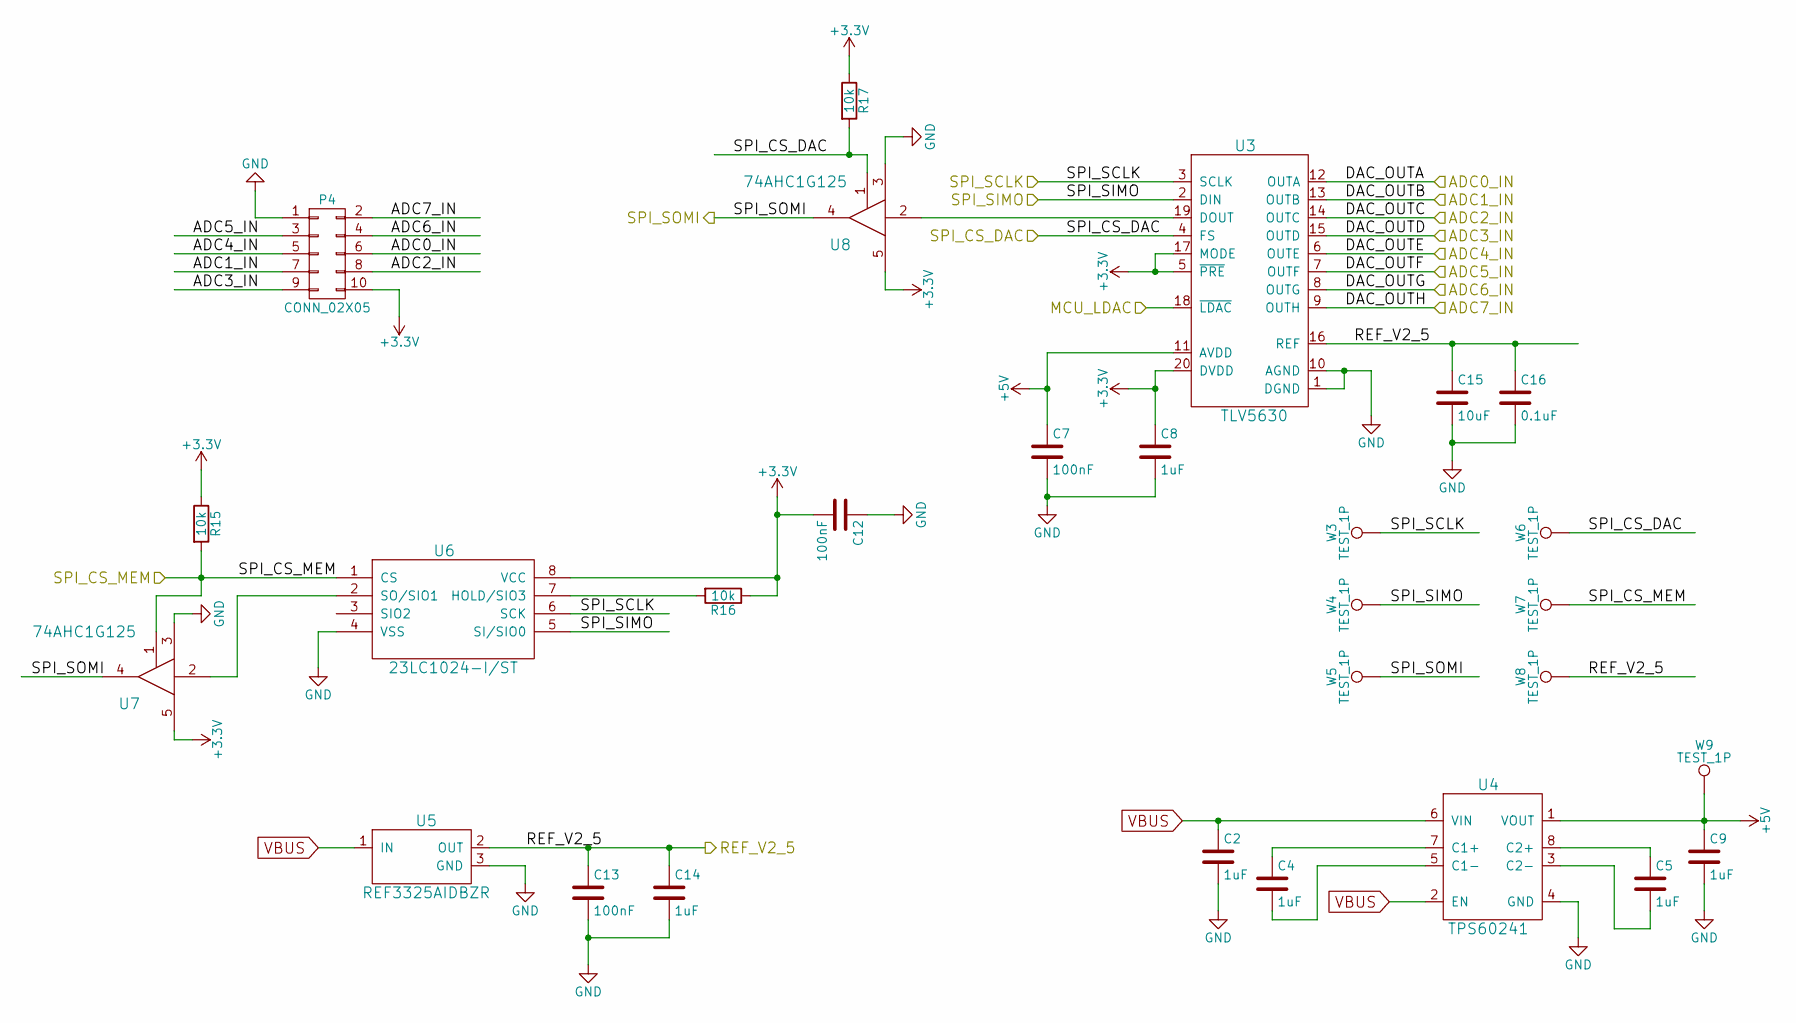
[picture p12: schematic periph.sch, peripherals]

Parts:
C2, C4, C5, C9: 1uF; C_0805_HandSoldering
C7, C12, C13: 100nF; C_0603_HandSoldering
C8, C14: 1uF; C_0603_HandSoldering
C15: 10uF; C_0603_HandSoldering
C16: 0.1uF; C_0603_HandSoldering
P4: CONN_02X05; Socket_Strip_Angled_2x05
R15, R16, R17: 10k; R_0603_HandSoldering
U3: TLV5630; TSSOP-20_4.4x6.5mm_Pitch0.65mm
U4: TPS60241; VSSOP8-DGK
U5: REF3325AIDBZR; SOT-23
U6: 23LC1024-I/ST; TSSOP-8_4.4x3mm_Pitch0.65mm
U7, U8: 74AHC1G125; SOT-353_SC-70-5_Handsoldering
W3, W4, W5, W6, W7, W8, W9: TEST_1P; TESTPAD_SMALL

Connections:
+3V3: C8.1, C12.2, P4.10, R15.1, R16.1, R17.1, U3.5 (~PRE), U3.17 (MODE), U3.20 (DVDD), U6.8 (VCC), U7.5, U8.5; also elsewhere on the board
+5V: C7.1, C9.1, U3.11 (AVDD), U4.1 (VOUT), W9.1
/mcu/ADC0_IN: P4.6, U3.12 (OUTA); also elsewhere on the board
/mcu/ADC1_IN: P4.7, U3.13 (OUTB); also elsewhere on the board
/mcu/ADC2_IN: P4.8, U3.14 (OUTC); also elsewhere on the board
/mcu/ADC3_IN: P4.9, U3.15 (OUTD); also elsewhere on the board
/mcu/ADC4_IN: P4.5, U3.6 (OUTE); also elsewhere on the board
/mcu/ADC5_IN: P4.3, U3.7 (OUTF); also elsewhere on the board
/mcu/ADC6_IN: P4.4, U3.8 (OUTG); also elsewhere on the board
/mcu/ADC7_IN: P4.2, U3.9 (OUTH); also elsewhere on the board
/mcu/MCU_LDAC: U3.18 (~LDAC); also elsewhere on the board
/mcu/REF_V2_5: C13.1, C14.1, C15.1, C16.1, U3.16 (REF), U5.2 (OUT), W8.1; also elsewhere on the board
/mcu/SPI_MISO: U7.4, U8.4, W5.1; also elsewhere on the board
/mcu/SPI_MOSI: U3.2 (DIN), U6.5 (SI/SIO0), W4.1; also elsewhere on the board
/mcu/SPI_SCLK: U3.3 (SCLK), U6.6 (SCK), W3.1; also elsewhere on the board
/periph/SPI_CS_DAC: R17.2, U3.4 (FS), U8.1, W6.1; also elsewhere on the board
/periph/SPI_CS_MEM: R15.2, U6.1 (CS), U7.1, W7.1; also elsewhere on the board
GND: C2.2, C7.2, C8.2, C9.2, C12.1, C13.2, C14.2, C15.2, C16.2, P4.1, U3.1 (DGND), U3.10 (AGND), U4.4 (GND), U5.3 (GND), U6.4 (VSS), U7.3, U8.3; also elsewhere on the board
unnamed: C4.1, U4.7 (C1+)
unnamed: C4.2, U4.5 (C1-)
unnamed: C5.1, U4.8 (C2+)
unnamed: C5.2, U4.3 (C2-)
unnamed: R16.2, U6.7 (HOLD/SIO3)
unnamed: U3.19 (DOUT), U8.2
unnamed: U6.2 (SO/SIO1), U7.2
VBUS: C2.1, U4.2 (EN), U4.6 (VIN), U5.1 (IN); also elsewhere on the board

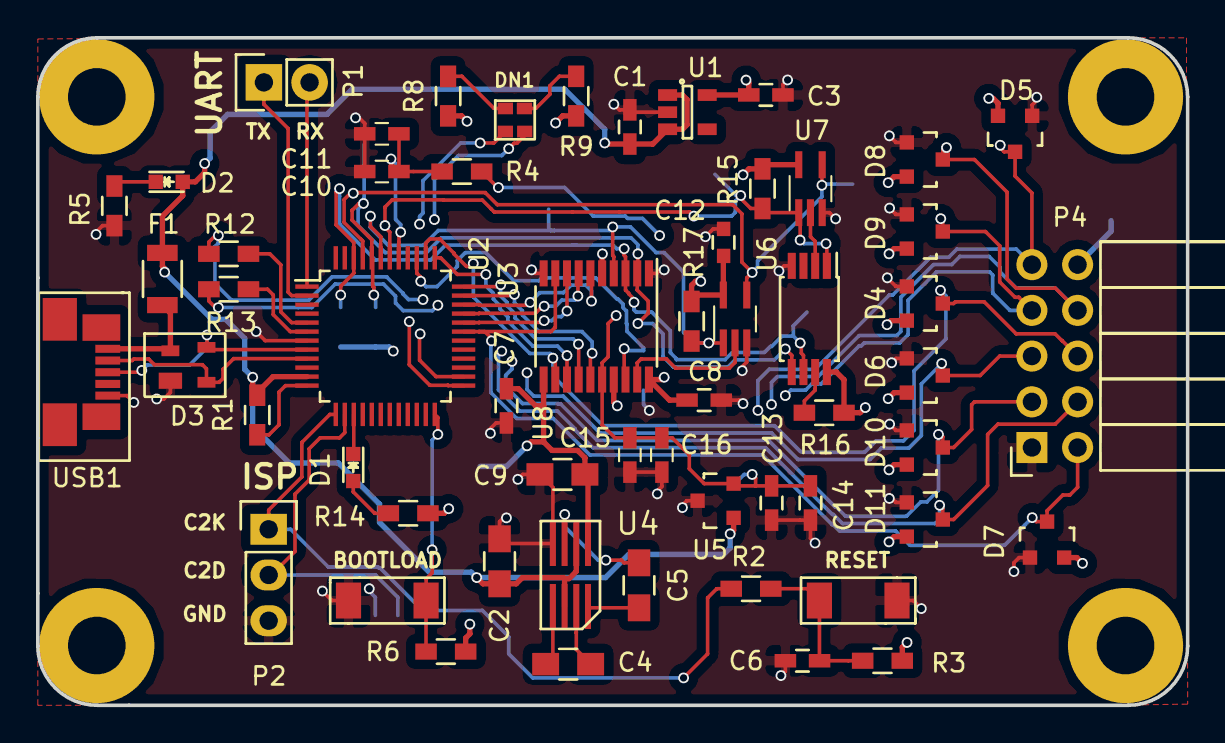
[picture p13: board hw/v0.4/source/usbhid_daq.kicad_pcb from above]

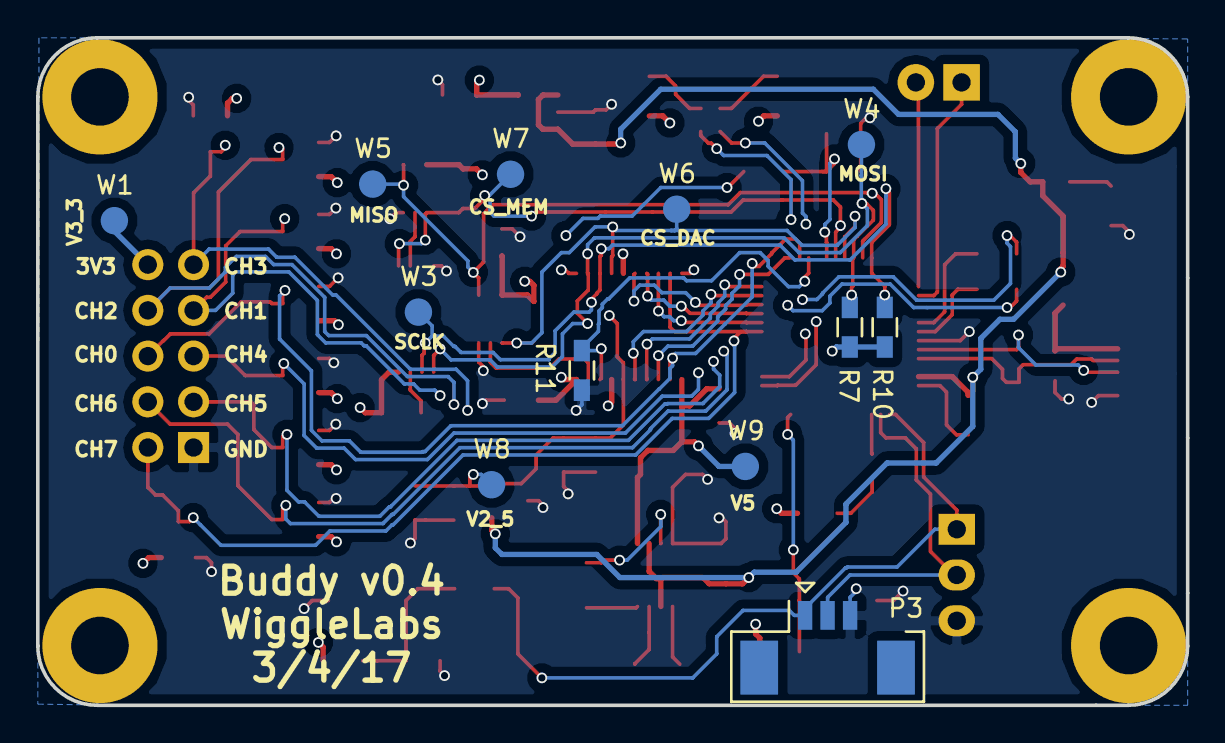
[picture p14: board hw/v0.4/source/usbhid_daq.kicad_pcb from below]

Board: 4 copper layers, 63.9 x 37.1 mm, 69 parts (12 on the bottom side), 46 nets.

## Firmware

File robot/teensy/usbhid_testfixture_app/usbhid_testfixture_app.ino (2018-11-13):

#include <string.h>

#include <ADC.h>
#include <SPI.h>
#include <IntervalTimer.h>
#include <RingBuffer.h>

#define USBHID_TESTFIXTURE_MAJOR_VER 0
#define USBHID_TESTFIXTURE_MINOR_VER 1

#define SERIAL_BUFFER_LENGTH 8192
#define ADC_SBUFFER_SIZE 8192
#define DAC_SBUFFER_SIZE 8192

// general
#define DAC_PIN A21

#define LED0_PIN 39
#define LED1_PIN 38

#define SPI_DOUT_PIN 11
#define SPI_DIN_PIN 12
#define SPI_SCLK_PIN 13
#define SPI_CS1_PIN 31
#define SPI_CS0_PIN 10

#define PWM_0_PIN 2
#define PWM_1_PIN 3
#define PWM_2_PIN 4
#define PWM_3_PIN 5
#define PWM_4_PIN 6
#define PWM_5_PIN 7
#define PWM_6_PIN 8
#define PWM_7_PIN 9

#define ADC_0_PIN 14
#define ADC_1_PIN 15
#define ADC_2_PIN 16
#define ADC_3_PIN 17
#define ADC_4_PIN 18
#define ADC_5_PIN 19
#define ADC_6_PIN 20
#define ADC_7_PIN 21

// DAC
#define DAC_MUX_SEL_A_PIN 24
#define DAC_MUX_SEL_B_PIN 25
#define DAC_MUX_SEL_C_PIN 26

#define DAC_MUX_EN_PIN 27

#define DAC_MUX_SEL_A_MASK 0x04
#define DAC_MUX_SEL_B_MASK 0x02
#define DAC_MUX_SEL_C_MASK 0x01

#define DAC_MUX_SEL_A_SHIFT 2
#define DAC_MUX_SEL_B_SHIFT 1
#define DAC_MUX_SEL_C_SHIFT 0

#define USBHID_BUDDY_PWM_CHANNELS 5

// ADC
// PWM
// Counter

const int ledPin = 13;

typedef enum _USBHID_TESTFIXTURE_MODE {
  USBHID_TESTFIXTURE_MODE_NONE = 0,
  USBHID_TESTFIXTURE_MODE_ADC,
  USBHID_TESTFIXTURE_MODE_SADC,
  USBHID_TESTFIXTURE_MODE_DAC,
  USBHID_TESTFIXTURE_MODE_SDAC,
  USBHID_TESTFIXTURE_MODE_PWM,
  USBHID_TESTFIXTURE_MODE_PWM_DUTY,
  USBHID_TESTFIXTURE_MODE_PWM_FREQ,
  USBHID_TESTFIXTURE_MODE_COUNTER,
} USBHID_TESTFIXTURE_MODE;

// ABC values for the selector lines tied to MAX4617 multiplexor
typedef enum _USBHID_TESTFIXTURE_DAC_SEL {
  USBHID_TESTFIXTURE_DAC_SEL_FIO_0 = 0x00,
  USBHID_TESTFIXTURE_DAC_SEL_FIO_1 = 0x04,
  USBHID_TESTFIXTURE_DAC_SEL_FIO_2 = 0x02,
  USBHID_TESTFIXTURE_DAC_SEL_FIO_3 = 0x06,
  USBHID_TESTFIXTURE_DAC_SEL_FIO_4 = 0x01,
  USBHID_TESTFIXTURE_DAC_SEL_FIO_5 = 0x05,
  USBHID_TESTFIXTURE_DAC_SEL_FIO_6 = 0x03,
  USBHID_TESTFIXTURE_DAC_SEL_FIO_7 = 0x07,
} USBHID_TESTFIXTURE_DAC_SEL;

typedef enum _TEENSY_PWM {
  TEENSY_PWM_0,
  TEENSY_PWM_1,
  TEENSY_PWM_2,
  TEENSY_PWM_3,
  TEENSY_PWM_4,
  TEENSY_PWM_5,
  TEENSY_PWM_6,
  TEENSY_PWM_7,
} TEENSY_PWM;

typedef enum _USBHID_CHANNELS {
  USBHID_CHANNELS_FIO_0 = 0,
  USBHID_CHANNELS_FIO_1,
  USBHID_CHANNELS_FIO_2,
  USBHID_CHANNELS_FIO_3,
  USBHID_CHANNELS_FIO_4,
  USBHID_CHANNELS_FIO_5,
  USBHID_CHANNELS_FIO_6,
  USBHID_CHANNELS_FIO_7
} USBHID_CHANNELS;

typedef enum _USBHID_TESTFIXTURE_MAX335_CS {
  USBHID_TESTFIXTURE_MAX335_CS_0 = 0,
  USBHID_TESTFIXTURE_MAX335_CS_1 = 1,
} USBHID_TESTFIXTURE_MAX335_CS;

typedef enum _USBHID_SERIAL_CHANNEL {
  USBHID_SERIAL_CHANNEL_0 = 0,
  USBHID_SERIAL_CHANNEL_1,
  USBHID_SERIAL_CHANNEL_2,
  USBHID_SERIAL_CHANNEL_3,
  USBHID_SERIAL_CHANNEL_4,
  USBHID_SERIAL_CHANNEL_5,
  USBHID_SERIAL_CHANNEL_6,
  USBHID_SERIAL_CHANNEL_7,
} USBHID_SERIAL_CHANNEL;

typedef enum _USBHID_SERIAL_ACTION {
  USBHID_SERIAL_ACTION_DISABLE = 0x00,
  USBHID_SERIAL_ACTION_ENABLE = 0x01,
} USBHID_SERIAL_ACTION;

// MAX335 switch state
// _0 = PWM
// _1 = ADC
static uint8_t max335_state_0 = 0;
static uint8_t max335_state_1 = 0;

static bool firstRun = true;

static uint8_t rxSerialBuffer[SERIAL_BUFFER_LENGTH] = { 0 };
static int rxSerialBufferOffset = 0;

const uint8_t buffer_size = 128;
DMAMEM static volatile int16_t __attribute__((aligned(buffer_size+0))) buffer[buffer_size] = {};

int readPin = A0;

int period0 = 10000; // us
int readPin0 = A0;

int readPeriod = 10000; // us

const int pwmPin = A0;

uint16_t adc_latest = 0;

ADC *adc = new ADC();

RingBuffer *buffer_sadc = new RingBuffer;
RingBuffer *buffer_sdac = new RingBuffer;

int prevTimeFall[USBHID_BUDDY_PWM_CHANNELS];
int prevTimeRise[USBHID_BUDDY_PWM_CHANNELS];

int deltaHigh[USBHID_BUDDY_PWM_CHANNELS];
int deltaLow[USBHID_BUDDY_PWM_CHANNELS];

IntervalTimer timer0;
int startTimerValue0 = 0;

volatile int adcStreamCount = 0;
volatile int adcStreamCountStop = 0;
volatile bool adcStreamFinish = false;

int pwmTickCount[USBHID_BUDDY_PWM_CHANNELS] = { 0 };

int testfixture_mode = USBHID_TESTFIXTURE_MODE_NONE;
bool adc_active = false;

int stream_loop_mode = 0;

int count = 0;

void pwm_set_freq_value(uint8_t channel, uint32_t value);
void pwm_set_duty_value(uint8_t channel, uint16_t value);

void heartbeat_led() {
  static int lastMillis = millis();

  if (((millis() % 1000) == 0) && (lastMillis != millis())) {
    lastMillis = millis();

    if (digitalRead(LED0_PIN) == HIGH) {
      digitalWrite(LED0_PIN, LOW);
    } else {
      digitalWrite(LED0_PIN, HIGH);
    }
  }
}

void activity_led() {
  if (digitalRead(LED1_PIN) == HIGH) {
    digitalWrite(LED1_PIN, LOW);
  } else {
    digitalWrite(LED1_PIN, HIGH);
  }
}

void timer0_callback(void) {
  adc->startSingleRead(readPin0, ADC_0); // also: startSingleDifferential, analogSynchronizedRead, analogSynchronizedReadDifferential

  uint16_t val;

  if (testfixture_mode == USBHID_TESTFIXTURE_MODE_SDAC) {
    if (!buffer_sdac->isEmpty()) {
      val = buffer_sdac->read();
      analogWrite(DAC_PIN, val);

      if (stream_loop_mode) {
        buffer_sadc->write(val);
      }
    }
  }
}

void adc0_isr() {
    uint8_t pin = ADC::sc1a2channelADC0[ADC0_SC1A&ADC_SC1A_CHANNELS]; // the bits 0-4 of ADC0_SC1A have the channel
    adc_latest = adc->readSingle();
    
    // restore ADC config if it was in use before being interrupted by the analog timer
    if (adc->adc0->adcWasInUse) {
        adc->adc0->loadConfig(&adc->adc0->adc_config);
        adc->adc0->adcWasInUse = false;
    }

    if ((testfixture_mode == USBHID_TESTFIXTURE_MODE_SADC) && (adc_active) && (!buffer_sadc->isFull())) {
      //Serial.println("trigger adc conversion");
      
      buffer_sadc->write(adc_latest);
      adcStreamCount++;
      
      if (adcStreamCount >= adcStreamCountStop) {
        //Serial.println("trigger finished");

        adc_active = false;
        adcStreamFinish = true;
      }
    }
}

void max4617_set_sel(uint8_t channel) {
  uint8_t a_pin_value, b_pin_value, c_pin_value;

  a_pin_value = ((channel & DAC_MUX_SEL_A_MASK) >> DAC_MUX_SEL_A_SHIFT);
  b_pin_value = ((channel & DAC_MUX_SEL_B_MASK) >> DAC_MUX_SEL_B_SHIFT);
  c_pin_value = ((channel & DAC_MUX_SEL_C_MASK) >> DAC_MUX_SEL_C_SHIFT);
 
  digitalWrite(DAC_MUX_SEL_A_PIN, a_pin_value);
  digitalWrite(DAC_MUX_SEL_B_PIN, b_pin_value);
  digitalWrite(DAC_MUX_SEL_C_PIN, c_pin_value);
}

void max335_enable_channel(uint8_t cs, uint8_t channel) {
  uint8_t temp_value;

  //Serial.println("max335_enable_channel A");

  temp_value = max335_state_0;
  temp_value |= (1 << channel);
  
  if (cs == USBHID_TESTFIXTURE_MAX335_CS_0) {
    temp_value = max335_state_0;
    temp_value |= (1 << channel);
    max335_state_0 = temp_value;

    //Serial.println("max335_enable_channel B");
    digitalWrite(SPI_CS0_PIN, LOW);
    //Serial.println("max335_enable_channel C");
    SPI.transfer(temp_value);
    //Serial.println("max335_enable_channel D");
    digitalWrite(SPI_CS0_PIN, HIGH);
    //Serial.println("max335_enable_channel E");
  } else if (cs == USBHID_TESTFIXTURE_MAX335_CS_1) {
    temp_value = max335_state_1;
    temp_value |= (1 << channel);
    max335_state_1 = temp_value;

    //Serial.println("max335_enable_channel F");
    digitalWrite(SPI_CS1_PIN, LOW);
    //Serial.println("max335_enable_channel G");
    SPI.transfer(temp_value);
    //Serial.println("max335_enable_channel H");
    digitalWrite(SPI_CS1_PIN, HIGH);
    //Serial.println("max335_enable_channel I");
  } else {
    //Serial.println("max335_enable_channel J");
    return;
  }
}

void max335_disable_channel(uint8_t cs, uint8_t channel) {
  uint8_t temp_value;

  if (cs == USBHID_TESTFIXTURE_MAX335_CS_0) {
    temp_value = max335_state_0;
    temp_value &= ~(1 << channel);
    max335_state_0 = temp_value;
    
    digitalWrite(SPI_CS0_PIN, LOW);
    SPI.transfer(temp_value);
    digitalWrite(SPI_CS0_PIN, HIGH);
  } else if (cs == USBHID_TESTFIXTURE_MAX335_CS_1) {
    temp_value = max335_state_1;
    temp_value &= ~(1 << channel);
    max335_state_1 = temp_value;
    
    digitalWrite(SPI_CS1_PIN, LOW);
    SPI.transfer(temp_value);
    digitalWrite(SPI_CS1_PIN, HIGH);
  } else {
    return;
  }
}

void set_mode(int mode) {
  switch (mode) {
    case USBHID_TESTFIXTURE_MODE_SADC:
    case USBHID_TESTFIXTURE_MODE_ADC:
      dac_mux_disable();
      pwm_mux_disable();
      
      adc_mux_enable();
      break;

    case USBHID_TESTFIXTURE_MODE_SDAC:
    case USBHID_TESTFIXTURE_MODE_DAC:
      adc_mux_disable();
      pwm_mux_disable();
      
      dac_mux_enable();   
      break;

    case USBHID_TESTFIXTURE_MODE_PWM_FREQ:
    case USBHID_TESTFIXTURE_MODE_PWM_DUTY:
      dac_mux_disable();
      adc_mux_disable();
      
      pwm_mux_enable();
      break;

    case USBHID_TESTFIXTURE_MODE_COUNTER:
      //dac_mux_disable();
      break;

     default:
      break;
  }
}

void pwm_set_duty_value(uint8_t channel, uint16_t value) {
  switch (channel) {
    case TEENSY_PWM_0:
      analogWrite(PWM_0_PIN, value);
      break;

    case TEENSY_PWM_1:
      analogWrite(PWM_1_PIN, value);
      break;

    case TEENSY_PWM_2:
      analogWrite(PWM_2_PIN, value);
      break;

    case TEENSY_PWM_3:
      analogWrite(PWM_3_PIN, value);
      break;

    case TEENSY_PWM_4:
      analogWrite(PWM_4_PIN, value);
      break;
      
    default:
      return;
  }
}

void pwm_set_freq_value(uint8_t channel, uint32_t value) {
  analogWriteFrequency(PWM_0_PIN, value);
  analogWriteFrequency(PWM_1_PIN, value);
}

void dac_mux_set_channel(uint8_t channel) {
  return max4617_set_sel(channel);
}

void pwm_mux_disable(void) {
  max335_disable_channel(USBHID_TESTFIXTURE_MAX335_CS_0, USBHID_CHANNELS_FIO_0);
  max335_disable_channel(USBHID_TESTFIXTURE_MAX335_CS_0, USBHID_CHANNELS_FIO_1);
  max335_disable_channel(USBHID_TESTFIXTURE_MAX335_CS_0, USBHID_CHANNELS_FIO_2);
  max335_disable_channel(USBHID_TESTFIXTURE_MAX335_CS_0, USBHID_CHANNELS_FIO_3);
  max335_disable_channel(USBHID_TESTFIXTURE_MAX335_CS_0, USBHID_CHANNELS_FIO_4);
  max335_disable_channel(USBHID_TESTFIXTURE_MAX335_CS_0, USBHID_CHANNELS_FIO_5);
  max335_disable_channel(USBHID_TESTFIXTURE_MAX335_CS_0, USBHID_CHANNELS_FIO_6);
  max335_disable_channel(USBHID_TESTFIXTURE_MAX335_CS_0, USBHID_CHANNELS_FIO_7);
}

void pwm_mux_enable(void) {
  // do nothing
}

void adc_mux_disable(void) {
  max335_disable_channel(USBHID_TESTFIXTURE_MAX335_CS_1, USBHID_CHANNELS_FIO_0);
  max335_disable_channel(USBHID_TESTFIXTURE_MAX335_CS_1, USBHID_CHANNELS_FIO_1);
  max335_disable_channel(USBHID_TESTFIXTURE_MAX335_CS_1, USBHID_CHANNELS_FIO_2);
  max335_disable_channel(USBHID_TESTFIXTURE_MAX335_CS_1, USBHID_CHANNELS_FIO_3);
  max335_disable_channel(USBHID_TESTFIXTURE_MAX335_CS_1, USBHID_CHANNELS_FIO_4);
  max335_disable_channel(USBHID_TESTFIXTURE_MAX335_CS_1, USBHID_CHANNELS_FIO_5);
  max335_disable_channel(USBHID_TESTFIXTURE_MAX335_CS_1, USBHID_CHANNELS_FIO_6);
  max335_disable_channel(USBHID_TESTFIXTURE_MAX335_CS_1, USBHID_CHANNELS_FIO_7);
}

void adc_mux_enable(void) {
  // do nothing
}

void dac_mux_disable(void) {
  digitalWrite(DAC_MUX_EN_PIN, HIGH);
}

void dac_mux_enable(void) {
  digitalWrite(DAC_MUX_EN_PIN, LOW);
}

void pwm_enable_channel(uint8_t channel) {
  return max335_enable_channel(USBHID_TESTFIXTURE_MAX335_CS_0, channel);
}

void pwm_disable_channel(uint8_t channel) {
  return max335_disable_channel(USBHID_TESTFIXTURE_MAX335_CS_0, channel);
}

void adc_enable_channel(uint8_t channel) {
  return max335_enable_channel(USBHID_TESTFIXTURE_MAX335_CS_1, channel);
}

void adc_disable_channel(uint8_t channel) {
  return max335_disable_channel(USBHID_TESTFIXTURE_MAX335_CS_1, channel);
}

uint16_t adc_get_value(uint8_t channel) {
  return adc->adc0->analogRead(channel);
}

void dac_init(void) {
  pinMode(DAC_MUX_SEL_A_PIN, OUTPUT);
  pinMode(DAC_MUX_SEL_B_PIN, OUTPUT);
  pinMode(DAC_MUX_SEL_C_PIN, OUTPUT);

  pinMode(DAC_MUX_EN_PIN, OUTPUT);
}
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

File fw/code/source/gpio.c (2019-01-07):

/**
 * @file gpio.c
 * @author Nicholas Shrake
 * @date 2 Oct 2015
 * @brief File containing GPIO routines for the 
 *  Silicon Labs C8051F380 device type.
 *
 */
 
#include "gpio.h"

/**
 * @brief initialize GPIO functionality
 * 
 */
void gpio_init()
{
	// red and green LEDs used to indicate RX/TX
	gpio_set_pin_mode(STATUS_TX_LED_PIN, GPIO_MODE_PUSH_PULL);
  gpio_set_pin_value(STATUS_TX_LED_PIN, GPIO_VALUE_HIGH);
    
	gpio_set_pin_mode(STATUS_RX_LED_PIN, GPIO_MODE_PUSH_PULL);
  gpio_set_pin_value(STATUS_RX_LED_PIN, GPIO_VALUE_HIGH);
	
	// heartbeat LED used to indicate if fw is running
	gpio_set_pin_mode(HEARTBEAT_PIN, GPIO_MODE_PUSH_PULL);
  gpio_set_pin_value(HEARTBEAT_PIN, GPIO_VALUE_LOW);
	
	// TLV563x LDAC low
	gpio_set_pin_mode(TLV563X_LDAC_PIN, GPIO_MODE_PUSH_PULL);
  gpio_set_pin_value(TLV563X_LDAC_PIN, GPIO_VALUE_LOW);
	
	// test/debug GPIO for measuring execution time
	gpio_set_pin_mode(TEST_STATUS_PIN, GPIO_MODE_PUSH_PULL);
	gpio_set_pin_value(TEST_STATUS_PIN, GPIO_VALUE_HIGH);
}

/** @brief Sets the pin value to high or low state.
  *
  *  @param pin Encoded pin value from gpio_drive_pins.
  *  @param value High or Low enum enumeration.
  *  @return error_t enum indicating success or error.
 */
int8_t gpio_set_pin_value(gpio_pin pin, gpio_value value)
{
    gpio_major_pin pin_major;
    gpio_minor_pin pin_minor;

    // use bitmask and shift operationt to extract
    // the major and minor positions
    pin_major = ((pin & GPIO_MAJOR_MASK) >> 3);
    pin_minor = (pin & GPIO_MINOR_MASK);
    
    switch (pin_major)
    {
        case GPIO_MAJOR_PORT0:
            P0 = (value == GPIO_VALUE_HIGH) ? (P0 | (1 << pin_minor)) : (P0 & ~(1 << pin_minor));
            break;
        
        case GPIO_MAJOR_PORT1:
            P1 = (value == GPIO_VALUE_HIGH) ? (P1 | (1 << pin_minor)) : (P1 & ~(1 << pin_minor));
            break;
        
        case GPIO_MAJOR_PORT2:
            P2 = (value == GPIO_VALUE_HIGH) ? (P2 | (1 << pin_minor)) : (P2 & ~(1 << pin_minor));
            break;
        
        case GPIO_MAJOR_PORT3:
            P3 = (value == GPIO_VALUE_HIGH) ? (P3 | (1 << pin_minor)) : (P3 & ~(1 << pin_minor));
            break;
        
        case GPIO_MAJOR_PORT4:
            P4 = (value == GPIO_VALUE_HIGH) ? (P4 | (1 << pin_minor)) : (P4 & ~(1 << pin_minor));
            break;
        
        // bad input, fail gracefully
        default:
            return GPIO_ERROR_CODE_INDEX_OUT_BOUND;
            break;
    }
    
    // otherwise, success
    return GPIO_ERROR_CODE_SUCCESS;
}
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

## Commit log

2017-03-19 1. reorg directory structure 2. add CMake build system 3. updates to fw to enable asycnc and poll-based updates for DAC and ADC types 4. removed python support
    [BOM.xlsx, buddy.obj, hid.obj, mcu.sch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]
2017-07-20 v0.4 pre-release
    [buddy.obj, hid.obj, support.obj, usbhid_buddy.obj]
2017-09-25 clean up for v0.4 release
    1. fix buddy version print
    2. use tsueno optimized 8051 assembly FIFO read/write routines (only use
    for SendPacket currently).
    3. introduce double IN_PACKET software buffer to allow higher ADC samples
    rate without having to block
    4. invoke the build packet routine directly in the ADC interrupt.
    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
2017-11-27 add better error handling framework
2018-08-12 robot framework integration update (#14)
    * fix pwm duty cycle; set dac and pwm_freq channel scripts; other fixes lost to sands of time
    * workspace commit
    * add get_adc_value script, more changes to simple python script
2018-10-02 minor updates, HID driver tweaking (#16)
    * remove uneeded files, add usb IN buffer clear
    * introduce clear method to flush USB IN buffer of results buffer read ADC
    * semi setable state, add batch script to repeat call adc read in stream mode, crank ADC sample up and watch in Beagle till we get near 2msec or so interrupt period
    * more debugging to find out why stream mode doesn't work if the latch off isn't enabled
    * add abuse read adc script
    * cleanup
2018-10-06 add CI & unit test framework (#18)
    * first try of travis ci build
    * fix script
    * add udev to build
    * update
    * update
    * remove env
    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
2018-10-26 add more unit tests (#20)
    * basic tests
    * begin encode unit tests
    * latest
    * update travis ci yml file
    * force print of gcc and g++ on console
    * latest travis file
    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
2018-10-29 add poncho expander board support (#21)
    * basic i2c single byte support working
    * unstaged changes from before
    * add poncho source files, remove debug stuff, tested and working on poncho v0.1 hardware mock up
    * clean up and more doxygen
    * add basic fields for poncho expander
    * start adding expander enum and field to buddy header
    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
2018-11-13 add robot framework test support (#23)
    * add robot framework and teensy software for v0.2
    * add test jig board files for v0.1 and v0.2 hardware
    * add v0.2 schematic pdf
    * rename adc dynamic test description
    [actives.sch, connectors.sch, usbhid_testfixture-B.Cu.gbl, usbhid_testfixture-B.Mask.gbs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]
2018-11-13 fix robot framework test suite names (#24)
    * change test suite names
    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
2019-01-21 first general rework and clean up (#27)
    * checkpoint
    * working
    * bring over origin rework branch changes
    * initial working with counter robot framework
    * commit
    * use different COM port for teensy in robot framework tests
    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
2019-02-15 improve unit test coverage (#31)
    * early unit test fixing
    * expand unit tests, add mock layer for buddy library
    * add hidapi_init unit test
    * add buddy_write_raw unit test
    * add buddy_write_packet unit test
    * update gitignore, add unit test for buddy_send_generic and buddy_read_packet
    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
